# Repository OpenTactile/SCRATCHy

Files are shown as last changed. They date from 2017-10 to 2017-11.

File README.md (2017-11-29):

# SCRATCHy  
The *SCalable Reference Architecture for a Tactile display Control Hardware*

SCRATCHy is an open hardware- and software-plattform for controlling so-called "tactile Displays", i. e. devices that are intended to stimulate the touch sensitive receptors in human skin. In combination with [ITCHy](https://github.com/OpenTactile/ITCHy), the tactile mouse, this project forms a complete research environment for e. g. developing new models controlling tactile displays or for conducting user studies.

This repository contains the following parts that reflect the folder structure:
  * `./pcb/` &rarr; Schematics and layouts for printed circuit boards
  * `./libSCRATCHy/` &rarr; Library to access the Signal Generators and peripherals
  * `./SCRATCHPy/` &rarr; Python wrapper covering the high-level functionality of libSCRATCHy
  * `./examplesCpp/` &rarr; Example programs using the C++ interface
  * `./examplesPython/` &rarr; Example programs using the Python interface
  * `./generatorFirmware/` &rarr; Signal Generator "operating system"

## Assembling the hardware system
The circuit boards located in the `./pcb/` folder have been designed with [Fritzing](http://fritzing.org/home/), an open source EDA software. For convenience, production ready [Extended Gerber](https://en.wikipedia.org/wiki/Gerber_format) files can be found in their respective subfolders.

Since most of the parts on the PCBs come in SMD packages, some experience in soldering such small parts is beneficial. However, the smallest components used here (0805 Package) can still be soldered by hand easily. (There are some nice [tutorial videos](https://www.youtube.com/watch?v=b9FC9fAlfQE) on how to solder SMD components by hand.)

Each of the PCB subfolders contains a Bill Of Material (BOM) listing the components required for a single board. The part numbers given in these lists can be looked up on [Farnell/Newark](http://www.farnell.com/).

#### System overview
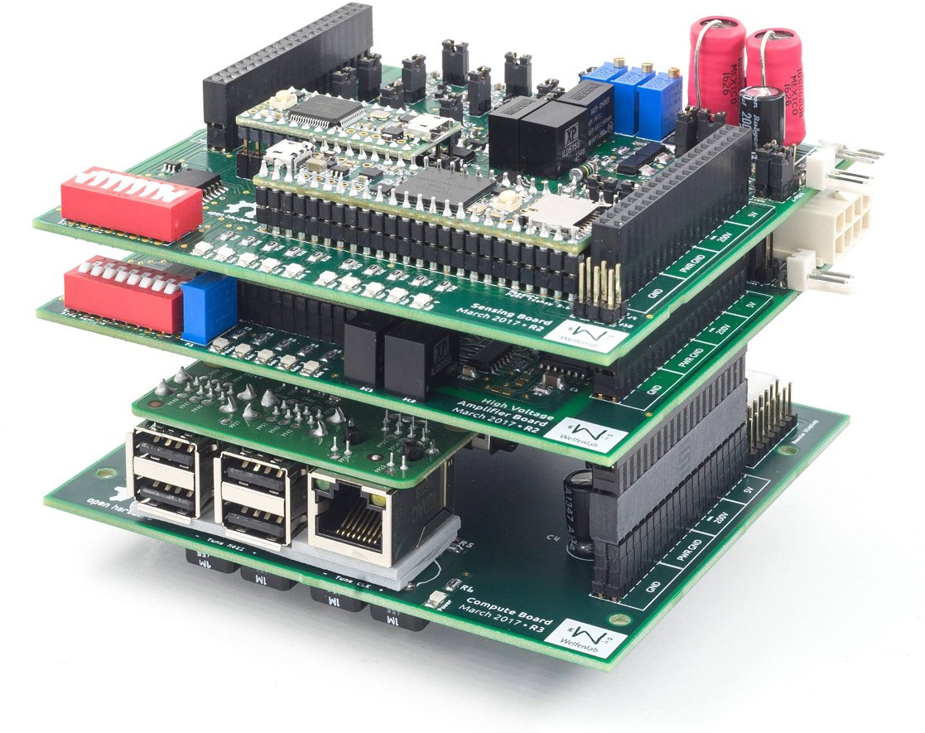
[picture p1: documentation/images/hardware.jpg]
Image of Yaktocat

The hardware system consists of a single main processor and several so-called *Signal Generators* (SGs) that are connected to a custom SPI/I²C bus. Each of these SGs is able to generate up to 4 indepentent analog signals. Depending of the type of SG, these signals can be amplified externally or are amplified onboard to up to &plusmn;200 V (theoretically, has been tested with 120V).

###### MainComputeUnit
The whole system builds upon the *MainComputeUnit* (MCU) that hosts a Raspberri Pi 3. This linux based computer is intended to generate - depending on e.g. position and velocity of the [Tactile Mouse](https://github.com/OpenTactile/ITCHy) - a rather abstract signal specification for each actuator of the tactile display that is distributed across the SPI bus. Finally, the connected SGs generate a continuous waveform that can be further amplified or processed.

The PCB exposes various GPIO pins as well as SPI and I²C ports of the Raspberry Pi 3 to a common data-bus. Additionally, the DisplayBreaktout board can be connected using a separate plug. This PCB also acts as a pedestal for other modules that can simply be stacked on top.  It can be fixated with four M3 screws.

###### DisplayBreakout
This optional PCB hosts a small graphical [OLED display](https://www.adafruit.com/product/931) as well as some tactile switches that can be accessed via ``libSCRATCHy``. It is connected to the MCU via I²C (and some GPIO pins used for the buttons). Since the Raspberry Pi 3 can connect via HDMI to an external monitor, this board is completely optional.

###### AnalogSignalGenerator
The AnalogSignalGenerator (ASG) contains two Signal Generators within one PCB and is therefore able to generate 8 analog output signals simultaneously. The control data sent from the MCU is interpreted using a custom software running on a [Teensy 3.2](https://www.pjrc.com/store/teensy32.html) USB development board and the resulting time-varying waveform is generated using [PWM](https://en.wikipedia.org/wiki/Pulse-width_modulation). This signal is then lowpass filtered to the frequency range relevant to the mechanoreceptors (0-1000 Hz).

###### HighVoltageAmplifier
The HighVoltageAmplifier (HVA) contains a single Signal Generator as well as a series of [Class-D amplifiers](https://en.wikipedia.org/wiki/Class-D_amplifier) in [H bridge](https://en.wikipedia.org/wiki/H_bridge) topology. Using a separate power supply (ranging from 0 to 200V max.) the PWM signals generated by the Teensy 3.2 are amplified to amplitudes of up to 200V (peak to peak, max.). In combination with a separate passive low pass filter, this signal may be used to drive e. g. piezoelectric actuators directly.

**Working with such high voltages is dangerous! A sufficient casing is needed to prevent accidential contact. Use at your own risk!**
This device has been tested for voltages up to 120 V. Depending on load and voltage, active cooling may be needed.

###### PiezoFilter
This board is needed for low-pass filtering the high voltage signals coming from the HVA. It contains several inductors that form in combination with the capacitivity of the piezoelectric actuators a sufficient filter.

## Programming the Signal Generators
Before the Teensy can be flashed, please install Teensyduino by following the [official instructions](https://www.pjrc.com/teensy/td_download.html). Afterwards, building and flashing the firmware is straightforward:

```shell
cd generatorFirmware
make
```
If the build process was successfull, you can install the firmware by connecting the Teensy (separate it from the SG board before!) via USB and running

```shell
make upload
```

## Dependencies
libSCRATCHy requires the following dependencies to be installed:
- [Qt 5.9](https://www.qt.io/)
- [libusb](http://libusb.info/)

If the Raspberry Pi 3 is going to be used for the MCU (recommended), the following libraries need to be installed as well:
- [Wiring Pi](http://wiringpi.com/)
- [libbcm2835](http://www.airspayce.com/mikem/bcm2835/)

SCRATCHPy, the python wrapper for libSCRATCHy, does need two more dependencies:
- Python 3.6m
- [Boost.Python](http://www.boost.org/doc/libs/1_65_1/libs/python/doc/html/index.html)

## Building libSCRATCHy and SCRATCHPy

libSCRATCHy uses the qmake build system and is available for linux platforms only. For building and installing the library system-wide, please follow these steps within the base directory:
```bash
mkdir libSCRATCHy-build
cd libSCRATCHy-build
qmake ../libSCRATCHy
make && sudo make install
```
#### Using *fake mode*
If you intend to use libSCRATCHy on a personal computer (not using the Raspberry Pi 3), you may pass an additional configuration option to qmake that disables some platform specific tests at runtime

```bash
[...]
qmake ../libSCRATCHy CONFIG+=fake
make && sudo make install
```
This also causes the ``iowrap_dummy.cpp`` to be built instead of ``iowrap_raspberry.cpp``. By using *fake mode*, one can make use of the complete SCRATCHy API without triggering any hardware specific actions (e.g. GPIO access, I²C communication, etc.).

## First steps in using libSCRATCHy
The directory `examplesCpp` contains a minimal example project that can be build using qmake:
```bash
mkdir minimalExample-build
cd minimalExample-build
qmake ../examplesCpp/minimalExample
make
./MinimalExample
```
Please make sure that libSCRATCHy as well as libITCHy has been build and installed beforehand.
This application will output a frequency that is scaled with the current movement speed of the tactile mouse.

## Interfacing with Python
A python-based application equivalent to the C++ example can be found in the `examplesPython` directory.
The python script `minimalExample.py` needs the python bindings of libSCRATCHy and libITCHy to be build.
When running
```bash
python minimalExample.py
```
the application should do exactly the same as the C++ example.

In case there are `ModuleNotFoundError` messages, please adjust the lines
```python
sys.path.append(os.path.abspath('../../SCRATCHPy/build/lib.linux-x86_64-3.6/'))
sys.path.append(os.path.abspath('../../../ITCHy/ITCHPy/build/lib.linux-x86_64-3.6/'))
```
to match the actual build-path of the libraries. 

## API Reference
The SCRACTHy API is separated into two categories: High- and Lowlevel functionality.
In the majority of cases, the Highlevel API should be sufficient to control the complete system. In case custom devices have been added to the bus-system, or if the SignalGenerators following a non-standard protocol, the Lowlevel API allows for direct access to GPIO, SPI and I²C.

### Highlevel API

#### GraphicalDisplay
This class allows accessing the (optional) DisplayBreakout by providing convenience functions for displaying icons and text.

##### `bool detach()`
Separates the GraphicalDisplay from the main thread, causing the `show` and `text` methods to be non-blocking.
However, special attention has to be drawn when communication via I²C from a different thread simultaneously.

##### `bool isPressed(Button button)`
Queries if a specific button is pressed *at the moment* of the call.
`Button` may be one of the following values:
- `Button::Back`
- `Button::Up`
- `Button::Down`
- `Button::Select` (The rightmost button on the DisplayBreakout)

##### `void clear()`
Clears the OLED Display causing all pixels to be set to black.

##### `void show(Icon icon, const std::string& header, const std::string& body)`
Renders a default arrangement to the OLED-display consisting of a small 32x32px pictogram on the left, a header text in a slightly larger font and a body text with the default 6x6px font. In case the strings are too long to be displayed they will be truncated.

The following pictograms can be selected:

None `Icon::None`, Scratchy `Icon::Scratchy`, Spectrum `Icon::Spectrum`, Forbidden `Icon::Forbidden`

Bolt `Icon::Bolt`, Bug `Icon::Bug`, Check `Icon::Check`, Clock `Icon::Clock`

Cog `Icon::Cog`, Fire `Icon::Fire`,  `Icon::Image`, Reboot `Icon::Reboot`

Power `Icon::Power`, Pulse `Icon::Pulse`, Random `Icon::Random`, Warning `Icon::Warning`

Wrench `Icon::Wrench`, X `Icon::X`

##### `void show(Icon icon, const std::string& header, float body)`
This is an overloaded method for quickly showing numerical values without the need for explicit string conversion.

##### `void text(const std::string& text)`
Displays the specified text on the OLED-display. In case the string is too long to be displayed in one line (21 characters) it will be wrapped automatically.

#### SignalManager
The `SignalManager` is responsible for initializing the individual SignalBoards correctly. It automatically enumerates all connected SignalBoards, assigns the correct I²C addresses and gives access to individual boards. For debugging purposes, error messages and general information will be printed to `std::cerr`.

##### `void maskDevice(uint8_t address)`
Excludes a specific I²C address from the enumeration process. This method can be called multiple times in order to mask more than one address. It can be used to permanently deactivate specific SignalBoards or in case additional I²C periphery has been added (e.g. the DisplayBreakout that will occupy the I²C address `0x3C`).

##### `bool initializeBoards(unsigned int dacResolution, unsigned int samplingTime)`
Resets all SignalBoards connected to the system and runs a "standard procedure" consisting of the following steps:

1. (global Reset)
2. Initialization of connected Signalboards
3. Assignment of I²C addresses according to the selected hardware address
4. Passing through the different runlevels of the SignalBoards and configuring the DAC resolution and sampling rate
5. Initiating the "running" state on all SignalBoards

The `samplingTime` is given in micro seconds and defaults to 62 µs resulting in a sampling rate of approximately 1/(62 µs) = 16 kHz.

##### `std::vector<uint8_t> scanDevices()`
Iterates over the whole (non masked) I²C address range and asks for an acknowledgment to the `SystemRequest::Alive` request. All properly initialized SignalBoards that respond to this request will be included in the returned list of I²C addresses.

##### `std::vector<SignalGenerator>& generators()`
Returns a list of all SignalGenerators that have been successfully enumerated.

##### `std::vector<uint8_t> addresses() const`
Returns a list of I²C addresses representing all active SignalBoards.

##### `SignalGenerator& generator(uint8_t address)`
Returns the `SignalGenerator` instance that maps to the specified address.
*Warning: Currently there are no checks if the address actually has been assigned.*

---

##### `void reset(uint8_t address)`
Causes a specific SignalBoard to be resetted.
*Warning: This method usually is called within the `initializeBoards` method. In most use cases, you probably do not want to call it manually.*

##### `void reset()`
Causes all (non masked) SignalBoard connected to the system to be resetted.
*Warning: This method usually is called within the `initializeBoards` method. In most use cases, you probably do not want to call it manually.*

##### `void initSystem()`
Initializes all SignalBoards that have been resetted beforehand, causing them to enter *Runlevel 0*
*Warning: This method usually is called within the `initializeBoards` method. In most use cases, you probably do not want to call it manually.*

##### `void assignAddresses()`
Iterates through all possible SignalGenerator addresses and assigns a new I²C address where applicable. Causes all `SignalGenerator` instances to be deleted an re-instanciated. Please make sure, the SignalGenerators have been resetted and initialized before this method is called.
*Warning: This method usually is called within the `initializeBoards` method. In most use cases, you probably do not want to call it manually.*

#### SignalGenerator

##### `uint8_t address() const`

##### `SystemStatus status() const`

##### `void resetStatus() const`

##### `bool isAlive()`

##### `void finishR0()`

##### `void finishR1()`

##### `void setDACResolution(uint8_t resolution)`

##### `void setSamplingRate(uint32_t rate)`

##### `void finishR2()`

##### `void startSignalGeneration() const`

##### `void send(const std::array<FrequencyTable, 4>& data)`

##### `void send(const FrequencyTable& dataABCD)`

##### `void send(const FrequencyTable& dataA, [...], const FrequencyTable& dataD)`

##### `void shutdown()`

#### PositionQuery

##### `virtual QVector2D position() const`

##### `virtual QVector2D velocity() const`

##### `virtual float orientation() const`

##### `virtual float angularVelocity() const`

##### `virtual bool buttonPressed() const`

##### `virtual bool initialize()`

##### `virtual void update()`

##### `virtual void feedback(unsigned char r, unsigned char g, unsigned char b)`

##### ConstantVelocityQuery

##### MousePositionQuery

### Lowlevel API
All lowlevel functions can be accessed via the `iowrap.h` header file. The lowlevel API gives access to platformspecific functionality such as GPIO configuration, direct SPI communication as well as sending custom I²C commands to the SignalBoards.

#### GPIO

##### `void GPIOSetDirection(unsigned int pin, GPIODirection direction)`

##### `void GPIOHigh(unsigned int pin)`

##### `void GPIOLow(unsigned int pin)`

##### `bool GPIOIsLow(unsigned int pin)`

##### `bool GPIOIsHigh(unsigned int pin)`

##### `void GPIOInit()`

##### `void GPIOFree()`

##### `void GPIOSetAddress(unsigned int address)`

##### `void GPIOSetBroadCast(bool value)`

#### SPI

##### `void SPIInit()`

##### `void SPIFree()`

##### `void SPISetDivider(unsigned int divider)`

##### `unsigned int SPIGetCurrentSpeed()`

##### `void SPISend(const uint16_t *data, int size)`

#### I²C

##### `void I2CInit()`

##### `void I2CFree()`

##### `bool I2CSetAddress(int address)`

##### `char I2CReadByte(int cmd)`

##### `bool I2CWriteByte(int cmd, unsigned char buffer)`

##### `bool I2CReadBlock(int cmd, uint16_t length, unsigned char *buffer)`

##### `bool I2CWriteBlock(int cmd, uint16_t length, const unsigned char* buffer)`

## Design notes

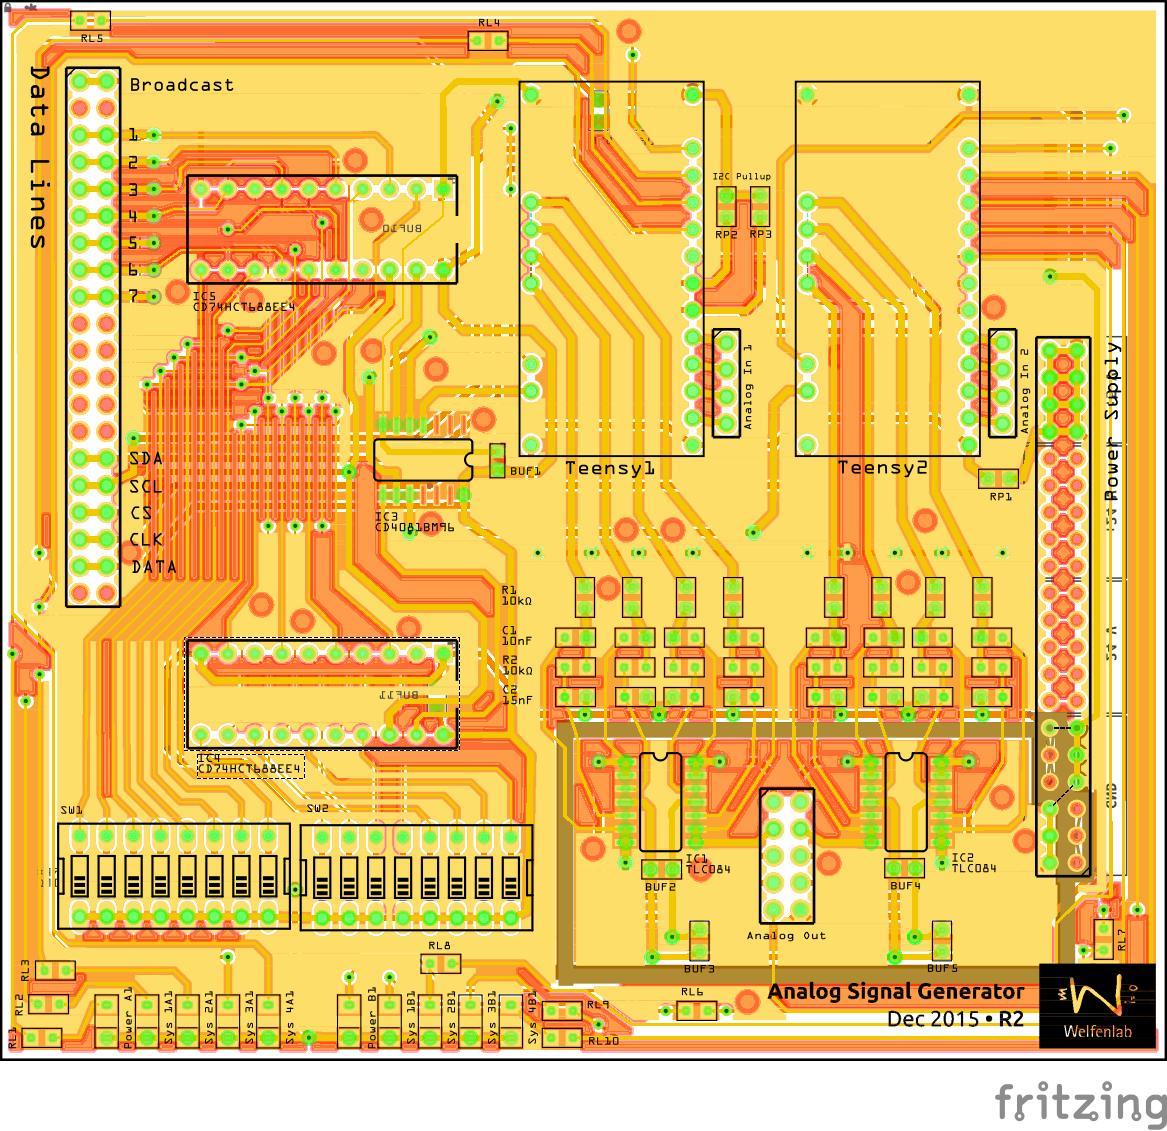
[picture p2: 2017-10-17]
pcb/AnalogSignalGenerator/AnalogSignalGenerator_Schematic.png

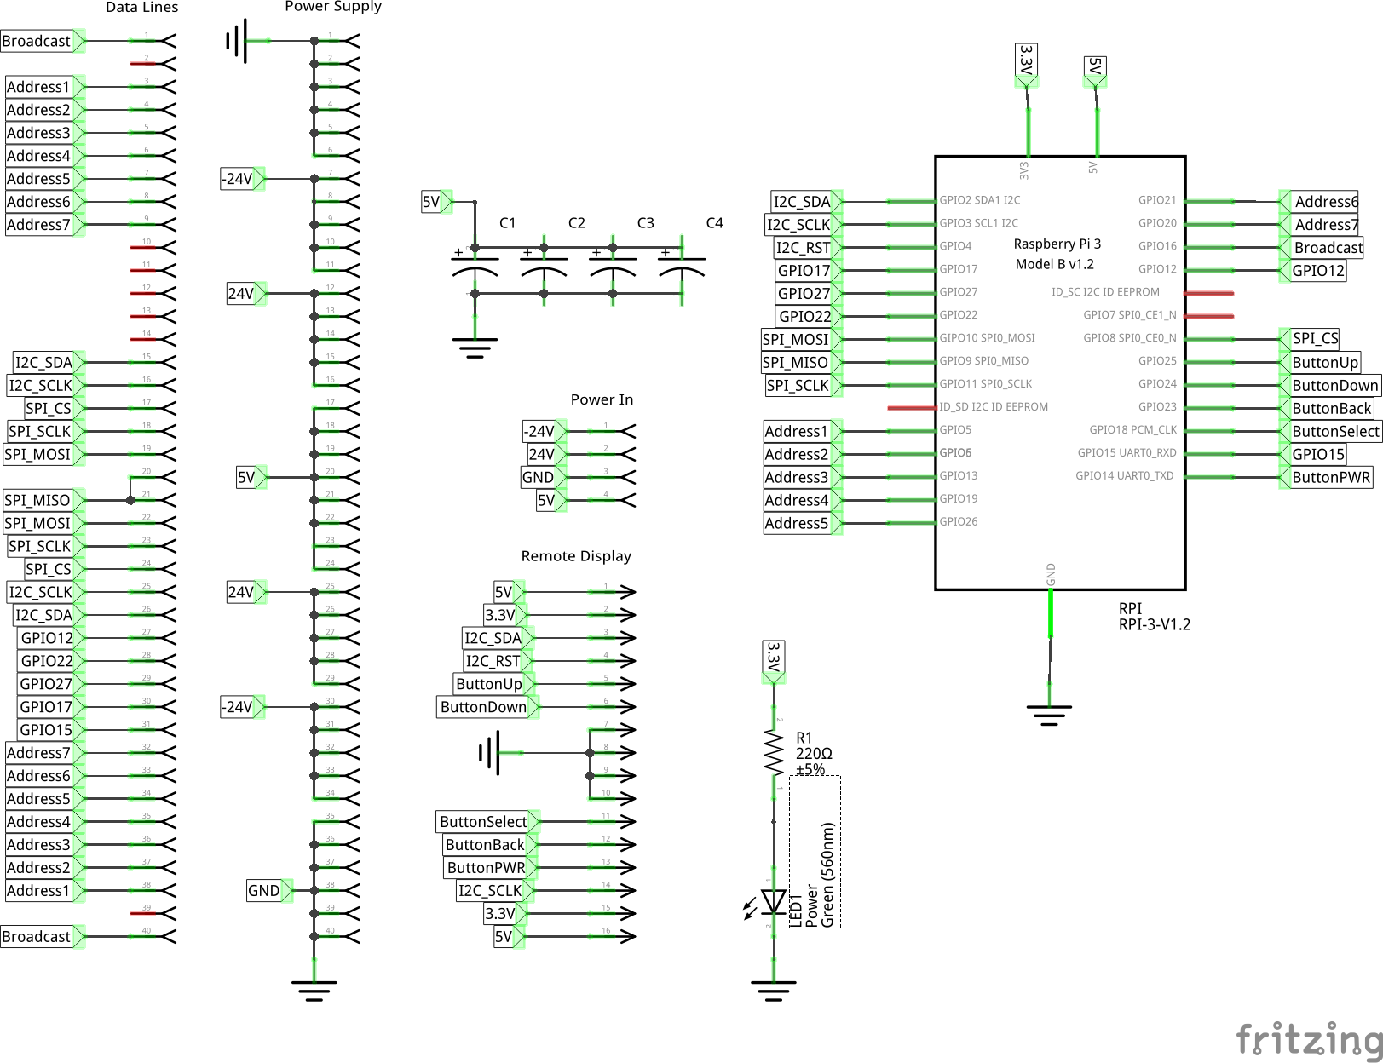
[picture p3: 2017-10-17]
pcb/MainComputeUnit/MainComputeUnit_Schematic.png

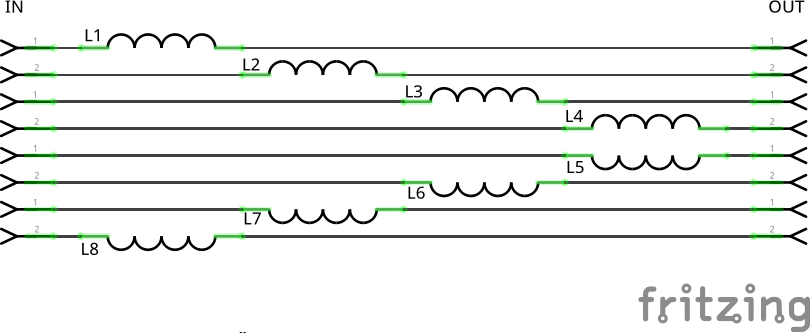
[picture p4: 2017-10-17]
pcb/PiezoFilter/PiezoFilter_Schematic.png

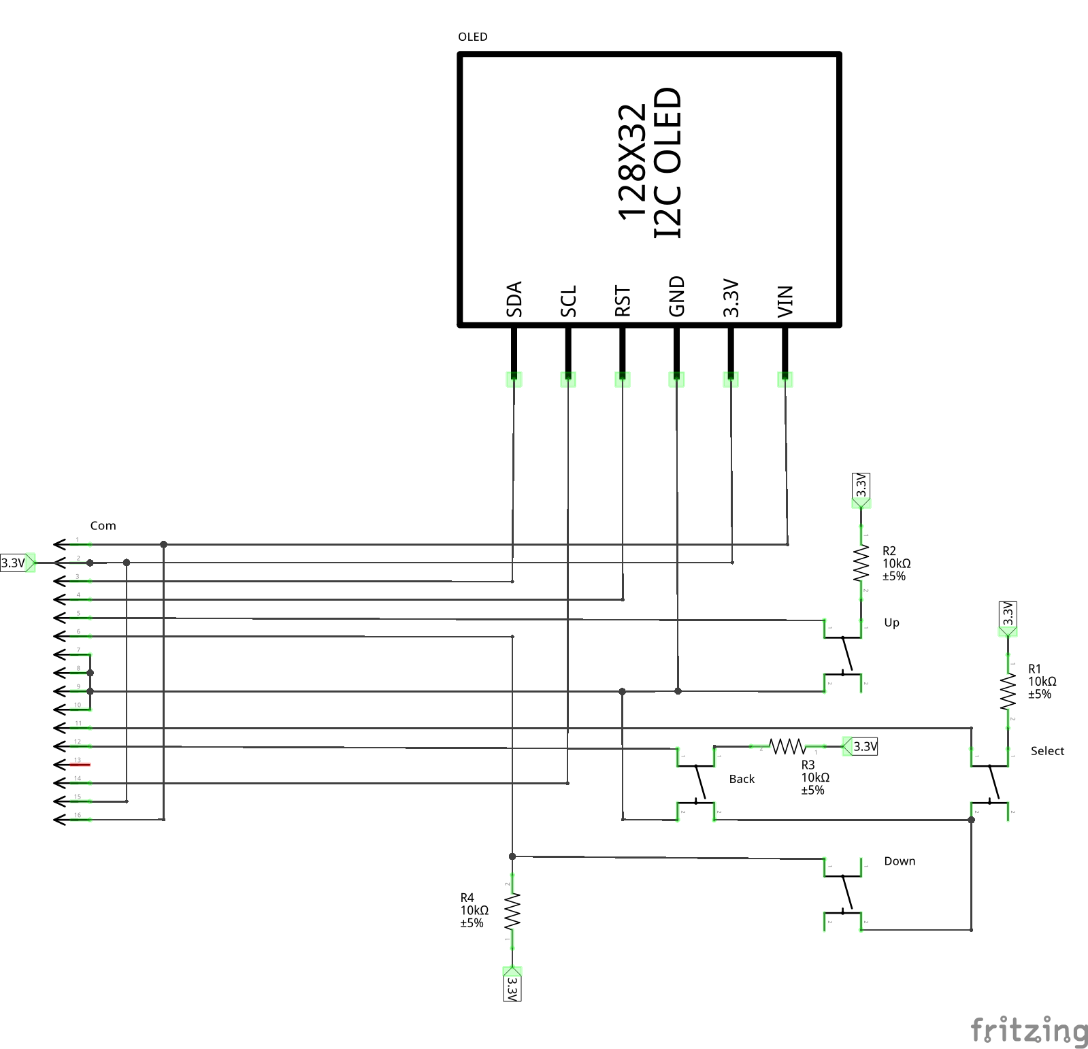
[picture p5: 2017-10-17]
pcb/DisplayBreakout/DisplayBreakout_Schematic.png

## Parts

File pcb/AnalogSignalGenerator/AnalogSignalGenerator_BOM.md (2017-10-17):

# Bill of Materials
## AnalogSignalBoard

### Assembly List
| Labels | Description | Package |
|-|-|-|
| Data Lines, Power Supply | Stacking Header, 2x20 Pins, Extra Tall  | THT |
| IC1, IC2 | Operational Amplifier, TLC084AID | SOIC-14 |
| IC3 | AND Gate, 8 inputs, CD4081BM96 | SOIC-14 |
| IC4, IC5 | Digital Comparator 8-bit, 74HC688 | DIP-20 |
| Teensy1, Teensy 2 | Teensy 3.2 USB Dev. Board | Custom |
| Teensy1, Teensy 2 | Low Profile Socket Strip, 14 Pins | THT |
| SW1, SW2 | Dip Switch, 8 Switches | THT |
| BUF1 - BUF11 | Capacitor, 0.1µF, 20 V | 0805 |
| RP* | Resistor, 1MOhm | 0805 |
| RL1 - RL10 | Resistor, 62Ohm | 0805 |
| RP1, RP2, RP3 | Optional Pullups - Do not use! | 0805 |
| Power A1, Power B1 | LED, Green | 1206 |
| Sys A, Sys B | LED, Yellow | 1206 |
| Analog out | Board to board connector, 10 Pins | THT |
| R1, R2 | Resistor, 10 kOhm | 0805 |
| C1 | Capacitor, 10 nF | 0805 |
| C2 | Capacitor, 15 nF | 0805 |

### Shopping List

| Amount | Part Type | Part Number | Farnell Nr. | Approx. Cost p.U. |
|-|-|-|-|-:|
|2| Stacking Header, 2x20 Pins, Extra Tall | 1979 | (Adafruit) | 2.50 € |
|2| Operational Amplifier, TLC084AID | TLC084AID | 1459730 | 3.41 € |
|1| AND Gate, 8 inputs, CD4081BM96 | CD4081BM96 | 2407128 | 0.35 € |
|2| Digital Comparator 8-bit, 74HCT688 | CD74HCT688E | 2407104 | 0.81 € |
|2| Teensy 3.2 USB Dev. Board | Teensy 3.2 | (PJRC) | 16.84 € |
|4| Low Profile Socket Strip, 14 Pins | SLW-114-01-G-S | 1668104 | 2.60 € |
|2| Dip Switch, 8 Switches | 76SB08T | 9479180 | 1.27 € |
|10| Capacitor, 0.1µF, 20 V | C2012X7R1H104K085AA | 2525147 | 0.11 € |
|16| Resistor, 1MOhm | MCWR08X1004FTL | 2447596 | 0.01 € |
|10| Resistor, 62Ohm | ERJ6GEYJ620V | 2323858 | 0.02 € |
|2| LED, Green | HSMG-C150. | 8554595 | 0.52 € |
|8| LED, Yellow | HSMY-C150. | 8554773 | 0.88 € |
|1| Board to board connector, 10 Pins | M20-7830546 | 7992009 | 1.06 € |
|16| Resistor, 10 kOhm | ERJ6GEYJ103V | 2057719 | 0.02 € |
|8| Capacitor, 10 nF | C2012C0G1E103J060AA | 2526251 | 0.22 € |
|8| Capacitor, 15 nF | C2012C0G1H153J085AA | 1907326 | 0.31 € |
|||| *Total Cost* | *76.49 €* |

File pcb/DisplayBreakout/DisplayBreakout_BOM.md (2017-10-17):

# Bill of Materials
## DisplayBreakout

### Assembly List
| Labels | Description | Package |
|-|-|-|
| Back, Down, Up, Select | Pushbutton | THT |
| OLED | I²C OLED Display, Adafruit 128x32 Pixel | THT |
| R1, R2, R3, R4 | Resistor, 10 kΩ | 0805 |
| Com | Double Row Male Header, 16 Pins, 2.54mm | THT |

### Shopping List

| Amount | Part Type | Part Number | Farnell Nr. | Approx. Cost p.U. |
|-|-|-|-|-:|
|4| Pushbutton | 430156050736 | 2402396 | 0.55 € |
|1| I²C OLED Display | 931 | (Adafruit) | 14.70 € |
|4| Resistor, 10 kΩ | MCMR08X103 JTL | 2073612 | 0.00136 € |
|1| Double Row Male Header | 61201621621 | 1642020 | 0.52 € |
|||| *Total Cost* | *17,43 €* |

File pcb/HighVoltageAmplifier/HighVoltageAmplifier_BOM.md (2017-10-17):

# Bill of Materials
## AnalogSignalBoard

### Assembly List
| Labels | Description | Package |
|-|-|-|
| Data Lines, Power Supply | Stacking Header, 2x20 Pins, Extra Tall  | THT |
| IC1 | H-Bridge driver, FAN73933MX | SOIC-14 |
| IC2 | Digital Comparator, CD74HCT688 | SOIC-20 |
| IC3 | AND Gate, 2 inputs, SN74LVC1G08 | SOT-23-5 |
| T1, T2 | Mosfet, n-Channel, 240V, BSP89,115 | SOT-223 |
| IC4 | Digital Isolator, SI8645BB-B-IS1 | NSOIC-16 |
| IC5 | Digital Inverter, SN74HC04D | SOIC-14 |
| DIP1 | Dip Switch, 8 Switches | THT |
| Teensy 3.2 | Teensy 3.2 USB Dev. Board | Custom |
| Teensy 3.2 | Low Profile Socket Strip, 14 Pins | THT |
| R9 | Resistor, 1 kOhm, 250V, 3W | 2512 |
| R1, R2, R3 | Resistor, 6.2 Ohm | 0805 |
| R4 | Resistor, 0 Ohm | 0805 |
| R5, R6 | Resistor, 10 kOhm | 0805 |
| R7 | Resistor, 1 MOhm | 0805 |
| R8 | Resistor, 62 Ohm | 0805 |
| D1 | Rectifier ultrafast, 400V, 50ns | DO-213AB |
| C1 | Capacitor, 4.7µF, 20V | 1206 |
| C2 | Capacitor, 0.47µF, 20V | 0805 |
| C3 | Capacitor, 10µF, 200V | THT |
| CBUF | Capacitor, 0.1µF, 20V | 0805 |
| Power | LED, Green | 1206 |
| Gen1 - Gen 4 | LED, Yellow | 1206 |
| DC1 | DC/DC Converter 5V/5V, 200mA | THT |
| DC2 | DC/DC Converter 5V/15V, 132mA | THT |
| P1 | Potentiometer (Optional) | THT |
| *not labeled* | 8 Pin Molex Connector | THT |
| *not labeled* | Pin Header, 3 Pins | THT |
| *not labeled* | Board to board Connector | THT |

### Shopping List

| Amount | Part Type | Part Number | Farnell Nr. | Approx. Cost p.U. |
|-|-|-|-|-:|
|2| Stacking Header, 2x20 Pins, Extra Tall | 1979 | (Adafruit) | 2.50 € |
|8| H-Bridge driver, FAN73933MX | FAN73933MX | 2083878 | 2.70 € |
|1| Digital Comparator, CD74HCT688 | CD74HCT688M96 | 2499926 | 0.88 € |
|1| AND Gate, 2 inputs, SN74LVC1G08 | SN74LVC1G08DBVR | 1287593 | 0.28 € |
|16| Mosfet, n-Channel, 240V, BSP89,115 | BSP89,115 | 1758087 | 0.25 € |
|1| Digital Isolator, SI8645BB-B-IS1 | SI8645BB-B-IS1 | 2423309 | 2.45 € |
|1| Digital Inverter, SN74HC04D | SN74HC04D | 9590943 | 0.40 € |
|1| Dip Switch, 8 Switches | 76SB08T | 9479180 | 1.27 € |
|1| Teensy 3.2 USB Dev. Board | Teensy 3.2 | (PJRC) | 16.84 € |
|2| Low Profile Socket Strip, 14 Pins | SLW-114-01-G-S | 1668104 | 2.60 € |
|8| Resistor, 1 kOhm, 250V, 3W | 35221K0FT | 2476488 | 0.84 € |
|24| Resistor, 6.2 Ohm | ERJ6GEYJ6R2V | 2323865 | 0.02 € |
|16| Resistor, 0 Ohm | ERJ6GEY0R00V | 2057661 | 0.02 € |
|16| Resistor, 10 kOhm | ERJ6GEYJ103V | 2057719 | 0.02 € |
|8| Resistor, 1MOhm | MCWR08X1004FTL | 2447596 | 0.01 € |
|5| Resistor, 62Ohm | ERJ6GEYJ620V | 2323858 | 0.02 € |
|8| Rectifier ultrafast, 400V, 50ns | EGL41G-E3/96 | 1336523 | 0.29 € |
|8| Capacitor, 4.7µF, 20V | GRM31CR71H475KA12L | 1735545 | 0.45 € |
|8| Capacitor, 0.47µF, 20V | C2012X7R1E474K125AA | 1907325 | 0.12 € |
|1| Capacitor, 10µF, 200V | 200PK10MEFC8X11.5 | 2346542 | 0.28 € |
|5| Capacitor, 0.1µF, 50V | C2012X7R1H104K085AA | 2525147 | 0.11 € |
|1| LED, Green | HSMG-C150. | 8554595 | 0.52 € |
|4| LED, Yellow | HSMY-C150. | 8554773 | 0.88 € |
|1| DC/DC Converter 5V/5V, 200mA | ROE-0505S | 2218597 | 2.49 € |
|1| DC/DC Converter 5V/15V, 132mA | IL0515S | 8728127 | 5.97 € |
|1| 8 Pin Molex Connector | 87427-0802 | 2313586 | 0.56 € |
|2| Pin Header, 3 Pins | 61300311121 | 2356154 | 0.06 € |
|1| Board to board Connector | 61900211021 | 1841368 | 0.43 € |
|||| *Total Cost* | *87.26 €* |

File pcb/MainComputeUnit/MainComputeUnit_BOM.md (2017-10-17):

# Bill of Materials
## MainComputeUnit

### Assembly List
| Labels | Description | Package |
|-|-|-|
| Data Lines, Power Supply | Stacking Header, 2x20 Pins, Extra Tall  | THT |
| Power In |  Molex Mini-Fit Jr, 4 Pins, 4.2 mm | THT |
| Remote Display | Double Row Male Header, 16 Pins, 2.54mm | THT |
| RPI | Board-to-Board Connector, 2x20 Pins, 2.54 mm | THT |
| RPI | Raspberry Pi 3 | THT |
| C1, C2, C3, C4 | Electrolytic Capacitor, 10µF, 8mm (optional) | THT |
| R1 | Resistor, 62 Ω| 0805 |
| LED1 | LED, Green, 20 mA, 2.2 V | 1206 |

### Shopping List

| Amount | Part Type | Part Number | Farnell Nr. | Approx. Cost p.U. |
|-|-|-|-|-:|
|2| Stacking Header, 2x20 Pins, Extra Tall | 1979 | (Adafruit) | 2.50 € |
|1| Molex Mini-Fit Jr, 4 Pins | 39303045 | 9963553 | 0.728 € |
|1| Double Row Male Header | 61201621621 | 1642020 | 0.52 € |
|1| Board-to-Board Connector, 2x20 Pins | ESQ-120-44-T-D | 2505030 | 6.62 € |
|1| Raspberry Pi 3 | RASPBERRYPI3-MODB-1GB | 2525225 | 30.19 € |
|4| Electrolytic Capacitor, 10µF (optional) | 200PK10MEFC8X11.5 | 2346542 | 0.284 € |
|1| Resistor, 62 Ω | ERJ6GEYJ620V | 2323858 | 0.0232 € |
|1| LED, Green | HSMG-C150. | 8554595 | 0.522 € |
|||| *Total Cost* | *44.74 €* |

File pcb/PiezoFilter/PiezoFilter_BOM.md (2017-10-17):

# Bill of Materials
## PiezoFilter

### Assembly List
| Labels | Description | Package |
|-|-|-|
| IN, OUT | Molex Mini-Fit Jr, 8 Pins, 4.2 mm | THT |
| L1, L2, L3, L4, L5, L6, L7, L8 | Inductor, 100 mH, 70 mA | THT |

### Shopping List

| Amount | Part Type | Part Number | Farnell Nr. | Approx. Cost p.U. |
|-|-|-|-|-:|
|2| Molex Mini-Fit Jr | 87427-0802 | 2313586 | 0.562 € |
|8| Inductor, 100 mH, 70 mA | IHD3EB104L | 1704136 | 3.81 € |
|||| *Total Cost* | *31.60 €* |

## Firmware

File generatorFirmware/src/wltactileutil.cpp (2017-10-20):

#include "wltactileutil.h"
#include <FastCRC.h>

#define HWSERIAL         Serial
#define BAUDRATE         9600

//#define DEBUG

// Restart Teensy: https://forum.pjrc.com/threads/24304-_reboot_Teensyduino()-vs-_restart_Teensyduino()?p=35985&viewfull=1#post35985
#define RESTART_ADDR       0xE000ED0C
#define READ_RESTART()     (*(volatile uint32_t *)RESTART_ADDR)
#define WRITE_RESTART(val) ((*(volatile uint32_t *)RESTART_ADDR) = (val))

void restart()
{
    WRITE_RESTART(0x5FA0004);
}

const unsigned long dacFreqTable[17] = {
         0, //  N/A
         0, //  N/A
  12000000, //  2 Bit PWM
   6000000, //  3 Bit PWM
   3000000, //  4 Bit PWM
   1500000, //  5 Bit PWM
    750000, //  6 Bit PWM
    375000, //  7 Bit PWM
    187500, //  8 Bit PWM
     93750, //  9 Bit PWM
     46875, // 10 Bit PWM
     23437, // 11 Bit PWM
     11718, // 12 Bit PWM
      5859, // 13 Bit PWM
      2929, // 14 Bit PWM
      1464, // 15 Bit PWM
       732, // 16 Bit PWM
};


volatile bool barrier = false;

void syncStep()
{
  noInterrupts();
  // Notify user if last loop took too long
  if(!barrier)
    wlTactileUtil::instance().timeout();

  // Release Lock
  barrier = false;
  interrupts();
}

void raiseThermal()
{
    noInterrupts();
    wlTactileUtil::instance().thermalWarning();
    interrupts();
}

void wlTactileUtil::init(void(*loop)())
{
    status = 0b0000;
    raisePanic = 0b1111;    

    //delay(2000);

    innerLoop = loop;

    // Configure outputs

    // PWM
    for(int n = 0; n < 4; n++)
        pinMode(PWMOut[n], OUTPUT);

    // System LEDs
    for(int n = 0; n < 4; n++)
        pinMode(LEDOut[n], OUTPUT);

    // Analog inputs
    for(int n = 0; n < 4; n++)
        pinMode(AnalogIn[n], INPUT);


    // Setup Heatwarning interrupt
    pinMode(HeatIn, INPUT);
    //attachInterrupt(HeatIn, raiseThermal, RISING);

    // Set Voltage to 0V
    R2_SetDACResolution(9);
    resetVoltages();

    // Short animation
    {
        setLED(0);
        digitalWrite(LEDOut[3],HIGH);
        delay(100);
        digitalWrite(LEDOut[2],HIGH);
        delay(100);
        digitalWrite(LEDOut[1],HIGH);
        delay(100);
        digitalWrite(LEDOut[0],HIGH);
        delay(100);
        setLED(0);
        delay(100);
        setLED(0b1111);
        delay(100);
        setLED(0);
        delay(100);
        setLED(0b1111);
        delay(100);
        setLED(0);
        delay(200);
    }

    currentRunlevel = 255;

#ifdef DEBUG
    HWSERIAL.print("dmaAddress#2: ");
    HWSERIAL.println((unsigned int)(&targetDMA[0]), HEX);
    HWSERIAL.print("dmaLength#2: ");
    HWSERIAL.println(targetDMASize, DEC);
#endif

    mainLoop();
}

void wlTactileUtil::initSPI2DMA(volatile unsigned char * volatile dmaMemory, unsigned int dmaMemoryLength)
{
    dma1.disable();

    delay(1000);
    if(!spiInitialized)
    {
        SIM_SCGC6 |= SIM_SCGC6_SPI0;
        delay(1000);
        SPI0_MCR = SPI_MCR_HALT;// | SPI_MCR_MDIS;
        SPI0_MCR |= SPI_MCR_DIS_RXF | SPI_MCR_DIS_TXF;  // Disable FIFOs
        SPI0_CTAR0_SLAVE = 0;
        SPI0_CTAR0_SLAVE |= SPI_CTAR_FMSZ(8 - 1);       // 8bit Mode
        SPI0_CTAR0_SLAVE = (SPI0_CTAR0_SLAVE & ~(SPI_CTAR_CPOL)); // SPI Mode 1
        SPI0_RSER = SPI_RSER_TFFF_DIRS | SPI_RSER_TFFF_RE |
                        SPI_RSER_RFDF_DIRS | SPI_RSER_RFDF_RE;
        // Configure muxes to use the right pins for SPI
        CORE_PIN13_CONFIG = PORT_PCR_MUX(2);
        CORE_PIN11_CONFIG = PORT_PCR_DSE | PORT_PCR_MUX(2);
        CORE_PIN12_CONFIG = PORT_PCR_MUX(2);
        CORE_PIN10_CONFIG = PORT_PCR_MUX(2);
        SPI0_MCR &= ~SPI_MCR_HALT; // Start

        dma1.source(SPI0_POPR);
    }
    dma1.destinationBuffer(dmaMemory, dmaMemoryLength);

#ifdef DEBUG
    HWSERIAL.print("dmaAddress: ");
    HWSERIAL.println((unsigned int)(&targetDMA[0]), HEX);

    HWSERIAL.println((unsigned int)(dmaMemory), HEX);
    HWSERIAL.print("dmaLength: ");
    HWSERIAL.println(dmaMemoryLength, DEC);
#endif

    if(!spiInitialized)
    {
        dma1.transferSize(1); // 8bit
        dma1.triggerAtHardwareEvent(DMAMUX_SOURCE_SPI0_RX);
    }
    dma1.enable();

    spiInitialized = true;
}


void wlTactileUtil::Init_Idle()
{
    idle_t += 0.05;
    if(idle_t > 2.0 * 3.1415)
        idle_t = 0.0;
    for(int n = 0; n < 4; n++)
    {
        float p = 255 * sin( 0.25* 3.1415 * n + 5*3.1415*sin(idle_t) + 3.1415) + 255;

        analogWrite(LEDOut[n], p);
    }

    delay(30);
}

void wlTactileUtil::Rp_Idle()
{
    setLED(0b0000);
    delay(50);
    setLED(status);
    delay(100);
    setLED(0b0000);
    delay(50);
    setLED(status);
    delay(800);
}

void wlTactileUtil::R4_Idle()
{
    idle_t += 0.025;
    for(int n = 0; n < 4; n++)
        analogWrite(LEDOut[n], 255 * sin(idle_t + 3.1415*0.25*n) + 255);
    delay(30);
}

void receiveI2C(size_t len)
{    
    noInterrupts();

    //Prevent timeout if interrupted
    wlTactileUtil::instance().R3_StopMainLoop();

#ifdef DEBUG
    HWSERIAL.print("\n\rI2C Received, length: ");
    HWSERIAL.println(len);
#endif

    unsigned short command = -1;
    unsigned int payload = 0;

    if(Wire.available() >= 1)
    {
        command = Wire.readByte();

#ifdef DEBUG
    HWSERIAL.print("Command: ");
    HWSERIAL.print(command, BIN);
    HWSERIAL.print(" (");
    HWSERIAL.print(command, HEX);
    HWSERIAL.println(")");
#endif
    }

    if(Wire.available() >= 4)
    {

        unsigned char pld[4] = {Wire.readByte(), Wire.readByte(),
                                Wire.readByte(), Wire.readByte()};

        payload = (((unsigned int)pld[0]) << (8*3)) +
                  (((unsigned int)pld[1]) << (8*2)) +
                  (((unsigned int)pld[2]) << (8*1)) +
                  (((unsigned int)pld[3]) << (8*0));


#ifdef DEBUG
    HWSERIAL.print("Payload: ");
    HWSERIAL.print(payload, DEC);
    HWSERIAL.print(" (");
    HWSERIAL.print(payload, HEX);
    HWSERIAL.println(")");
#endif
    }


    while(Wire.available())
        Wire.readByte(); // Drop remaining data


    if(command != -1)
        wlTactileUtil::instance().processCommand(command, payload);

    barrier = true;
    interrupts();
}

void requestI2C(void)
{
    noInterrupts();
    wlTactileUtil::instance().processRequest();
    barrier = true;
    interrupts();
}

void wlTactileUtil::initI2C(unsigned int address)
{
    Wire.begin(I2C_SLAVE, address, I2C_PINS_18_19, I2C_PULLUP_EXT, I2C_RATE_100);
    Wire.onReceive(receiveI2C);
    Wire.onRequest(requestI2C);

#ifdef DEBUG
    HWSERIAL.print("I2C initialized, address: ");
    HWSERIAL.println(address);
#endif
}

void wlTactileUtil::processCommand(unsigned short command, unsigned int payload)
{
    lastCommand = command;

    // Global commands:

    if(command == SystemRequest::Reset)
    {
        restart();
        return;
    }

    if(command == SystemRequest::Alive)
    {
#ifdef DEBUG
    HWSERIAL.println("Alive requested");
#endif
        return;
    }
    if(command == SystemRequest::Status)
    {
#ifdef DEBUG
    HWSERIAL.println("Status requested");
#endif
        return;
    }
    if(command == SystemRequest::StatusReset)
    {
        status = 0;
        return;
    }

    switch(currentRunlevel)
    {
    case 255:
        if(command == SystemRequest::InitSystem)
            currentRunlevel = 0;
        break;

    case 0: // Address initialization
        if(command == SystemRequest::FinishR0)
            currentRunlevel = 1;

        if(command == SystemRequest::SetI2CAddress)
        {
            // Set new Adress
            bool rightOne = false;

#ifdef DEBUG
    HWSERIAL.print("SCL is: ");
    HWSERIAL.println(digitalRead(10));
#endif
            rightOne = (digitalRead(10) == LOW);
            if(rightOne)
                initI2C(payload);
        }

        break;

    case 1: // SPI test
        if(command == SystemRequest::FinishR1)
            currentRunlevel = 2;
        if(command == SystemRequest::SPIPrepare)
        {
            asm volatile ("dsb");
            dma1.destinationBuffer(crcDMA, crcDMASize);
        }

        break;

    case 2: // Configuration
        if(command == SystemRequest::FinishR2)
            currentRunlevel = 3;

        if(command == SystemRequest::SetDACResolution)
            R2_SetDACResolution(payload);

        if(command == SystemRequest::SetPanicMask)
            R2_SetPanicMask(payload);

        if(command == SystemRequest::SetSamplingRate)
            R2_SetSamplingRate(payload);

        break;

    case 3: // Signalloop
        if(command == SystemRequest::FinishR3)
            currentRunlevel = 4;

        break;

    case 5: // Recovery
        if(command == SystemRequest::FinishRecovery)
            currentRunlevel = 3;

        break;
    }
}

void wlTactileUtil::processRequest()
{
    // The current status can be acquired at any time
    if(lastCommand == SystemRequest::Status)
    {        
        Wire.write(status);
        return;
    }

    switch(currentRunlevel)
    {
    case 1: // SPI test
        if(lastCommand == SystemRequest::SPIChecksum)
        {
            unsigned long crc = checkCRC32();
            Wire.write(&((byte*)(&crc))[0], 4);
            return;
        }
        break;
    }
}

unsigned long wlTactileUtil::checkCRC32()
{
    FastCRC32 crc32;
    #ifdef DEBUG
    HWSERIAL.println("\nCRC32 Data:");
    for(int n = 0; n < crcDMASize; n++)
    {
        HWSERIAL.print((unsigned int)(crcDMA[n]), DEC);
        HWSERIAL.print(" ");
    }
    #endif

    return crc32.crc32(const_cast<const unsigned char*>(crcDMA), crcDMASize);
}

volatile unsigned char * volatile wlTactileUtil::requestDMABuffer(unsigned int bufferSize)
{
#ifdef DEBUG
    HWSERIAL.begin(BAUDRATE);
    HWSERIAL.println("DMA request");
#endif

    if(targetDMA)
        delete[] targetDMA;

    targetDMA = new volatile unsigned char[bufferSize];
    targetDMASize = bufferSize;

#ifdef DEBUG
    HWSERIAL.println("Initialized DMA buffer:");
    HWSERIAL.print("dmaAddress: ");
    HWSERIAL.println((unsigned int)(&targetDMA[0]), HEX);
    HWSERIAL.print("dmaLength: ");
    HWSERIAL.println(targetDMASize, DEC);
#endif

    return &targetDMA[0];
}

void wlTactileUtil::mainLoop()
{
    while(true)
    {
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

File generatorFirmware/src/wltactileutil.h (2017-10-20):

#ifndef WLTACTILEUTIL_H
#define WLTACTILEUTIL_H

#include "WProgram.h"
#include "DMAChannel.h"

#include <i2c_t3.h>
#include <core_pins.h>

#define ARM_MATH_CM4
#include <arm_math.h>

class wlTactileUtil
{
public:
    static wlTactileUtil& instance()
    {
        static wlTactileUtil _instance;
        return _instance;
    }

    ~wlTactileUtil(){}

    enum class SystemLED
    {
        Alive     = 0,
        Sync      = 1,
        Data      = 2,
        Interrupt = 3
    };

    enum class SystemStatus
    {
        Operational    = 0b0000,
        ThermalWarning = 0b0010,
        NotInSync      = 0b0100,
        ConfigInvalid  = 0b1000
    };

    enum SystemRequest
    {
        // Can be received at any time
        Reset               = 0b11111111, // Performs a soft-reset using _reboot_Teensyduino_()

        // Can be received at any time
        Alive               = 0b00000000,
        Status              = 0b00000001,
        StatusReset         = 0b00000011,

        // Runlevel 0:
        // The Signalboard just has been booted, the internal I2C address
        // is set to 0b0000000 till the mainboard sets a new one.
        // A new address is only set if SCK is low after 'SetI2CAddress'
        // has been sent.
        FinishR0            = 0b00011111, // Advance to runlevel 1
        SetI2CAddress       = 0b00010000, // 2nd Byte contains the new address

        // Runlevel 1:
        // Performance measurements are taken out to determine the maximum
        // reliable speed for SPI communication. Several packages of 1kByte
        // size are sent by the mainboard via SPI and a checksum (CRC32) is
        // requested. This test can be performed several times.
        // FIXME: This code has not been tested yet
        //        due to problems with resetting SPI communication
        FinishR1            = 0b00101111, // Advance to runlevel 2
        SPIPrepare          = 0b00100001,
        SPIChecksum         = 0b00100000, // Calculate and send back CRC32 checksum

        // Runlevel 2:
        // Configuration of the signalgenerator
        FinishR2            = 0b00111111, // Advance to runlevel 3
        SetSamplingRate     = 0b00110000,
        SetDACResolution    = 0b00110001,
        SetPanicMask        = 0b00110010,

        // Runlevel 3:
        // Run the frequency generator
        FinishR3            = 0b01001111, // Advance to runlevel 4
        StartLoop           = 0b01000000,

        // Runlevel 4:
        // No operations are carried out at runlevel 4.
        // This mode is used after powering down the mainboard
        // Only 'Reset' and Status commands are accepted.

        // Runlevel R (5):
        // Recovery state: Whenever the SPI transfer is out of sync, the Teensy
        // switches to "recovery mode" allowing to resync with the mainboard
        FinishRecovery      = 0b01011111,

        // Runlevel P (6):
        // Panic: A fatal error has occured, no further operation is performed
        // till the module has been resetted

        // Runlevel -1:
        // Wait for wakeupcall from main board
        InitSystem          = 0b10101010
    };

    // Some animations...
    void Init_Idle();
    void R4_Idle();
    void Rp_Idle();

    void R1_PrepareDMATest();

    void R2_SetDefaults();
    void R2_SetSamplingRate(unsigned int samplingRate);
    void R2_SetDACResolution(unsigned char dacBits);
    void R2_SetPanicMask(unsigned char mask);

    void R3_StartMainLoop();
    void R3_StopMainLoop();

    volatile unsigned char * volatile requestDMABuffer(unsigned int bufferSize);
    void init(void(*loop)());

    inline void analogOut(unsigned char output, int value)
    {        
        analogWrite(PWMOut[output], value);
    }

    template<unsigned char OUT>
    inline void analogOutQ15(q15_t valueFixed)
    {
        const uint32_t bits = this->dacBits;
        uint32_t value = (int(valueFixed) >> (15 - (bits - 1))) + ((1 << (bits-1)) - 1);

        const char FTM1_CH0_PIN = 3;
        const char FTM1_CH1_PIN = 4;
        const char FTM0_CH7_PIN = 5;
        const char FTM0_CH4_PIN = 6;
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

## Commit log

2017-08-23 Added DisplayBreakout PCB
    [DisplayBreakout.fzz]
2017-08-23 Add (optional) pullup resistors to DisplayBreakout
    [DisplayBreakout.fzz]
2017-08-28 Add gerber files for DisplayBreakout
    [DisplayBreakout_contour.gm1, DisplayBreakout_copperBottom.gbl, DisplayBreakout_copperTop.gtl, DisplayBreakout_maskBottom.gbs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]
2017-08-28 Add schematic of DisplayBreakout
    [DisplayBreakout.fzz]
2017-08-28 Add PiezoFilter PCB files
    [PiezoFilter.fzz, PiezoFilter_contour.gm1, PiezoFilter_copperBottom.gbl, PiezoFilter_copperTop.gtl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]
2017-08-28 Add MainComputeUnit PCB files
    [MainComputeUnit.fzz, MainComputeUnit_contour.gm1, MainComputeUnit_copperBottom.gbl, MainComputeUnit_copperTop.gtl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]
2017-08-28 Add HighVoltageAmplifier PCB, WIP
    [HighVoltageAmplifier.fzz]
2017-08-28 Add example Project Stub and get everything compiling
    Needed to separate DisplayDetachable since QObject is used here.
    This should be replaced at a later time in favor of using std::threads.
2017-08-29 (fix) started to repair schematic
    [HighVoltageAmplifier.fzz]
2017-08-30 Clean up HVA PCB a little bit
    [HighVoltageAmplifier.fzz]
2017-08-31 (feat) nice printing, little refactoring
2017-10-17 Add Gerber files for HVA
    [HighVoltageAmplifier_contour.gm1, HighVoltageAmplifier_copperBottom.gbl, HighVoltageAmplifier_copperTop.gtl, HighVoltageAmplifier_maskBottom.gbs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]
2017-10-17 Add AnalogSignalGenerator pcb
    [AnalogSignalGenerator.fzz]
2017-10-17 Add Gerber files for ASG
    [AnalogSignalGenerator_contour.gm1, AnalogSignalGenerator_copperBottom.gbl, AnalogSignalGenerator_copperTop.gtl, AnalogSignalGenerator_maskBottom.gbs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]
2017-10-17 Correct ASB schematic to reflect nomenclature in BOM
    [AnalogSignalGenerator.fzz]
2017-10-20 Update README.md Describe the purpose of individual PCBs
2017-10-20 Add SignalGenerator firmware Migrated from former internal git repo. Adjusted makefile to use system installation of teensyduino.
